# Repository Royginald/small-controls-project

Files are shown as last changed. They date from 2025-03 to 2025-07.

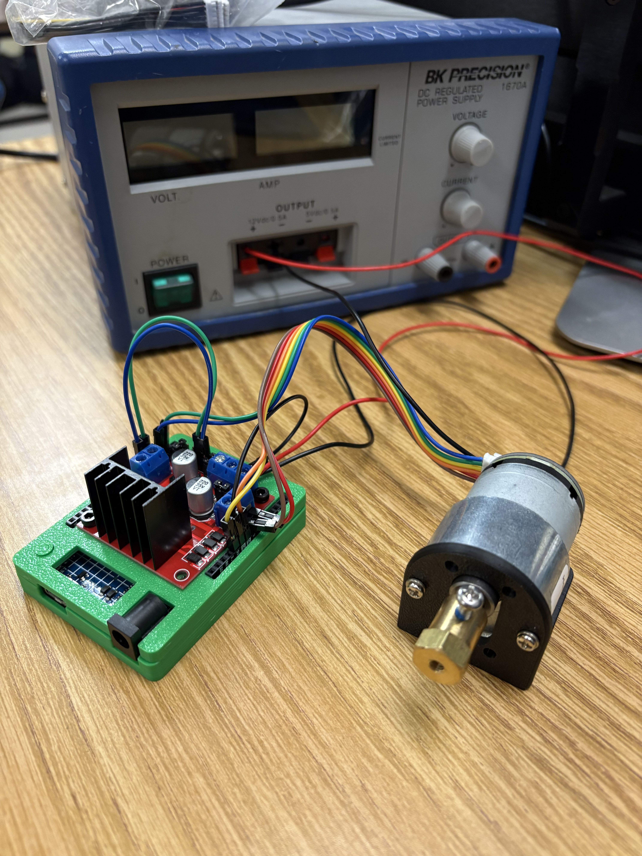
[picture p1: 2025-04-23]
wiring_setup/ArduinoPlant2.jpeg

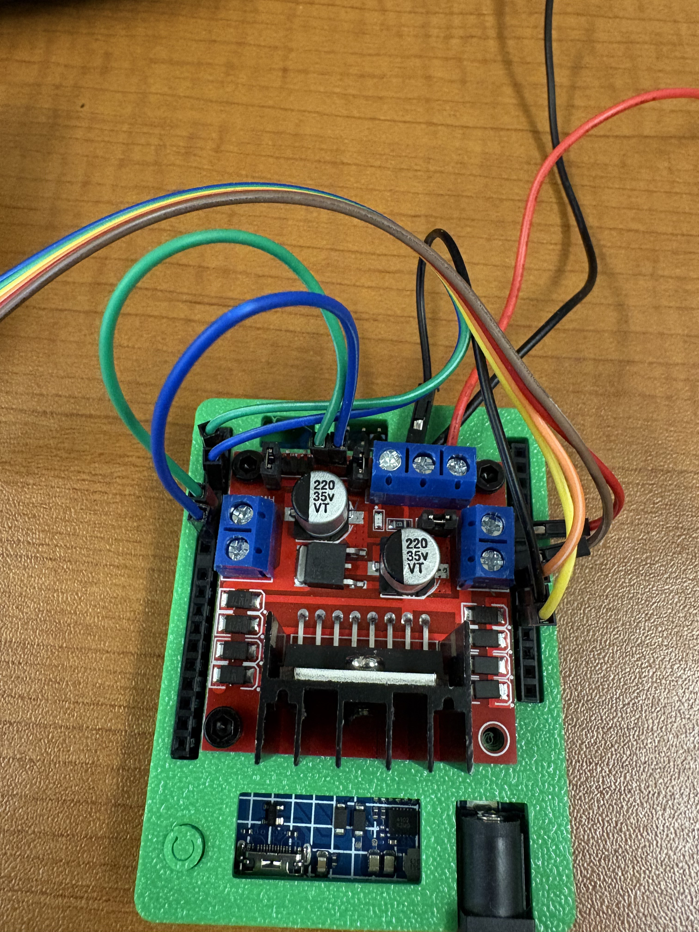
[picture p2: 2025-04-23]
wiring_setup/ArduinoPlant1.jpeg

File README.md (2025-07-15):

This repository documents the motor plants that were made for the use of the Inteligent Controls and Injetion moldling lab an UNB.

This repository conains:
 - The CAD files needed to 3D print the brackets for the motor (cad)
 - The wiring digram used to wire the Arduino R4 to the motor and motor driver (wiring_setup)
 - An Arduino program to control the motor from an Ardino R4 (Motor_Control)
 - Some sample responses (in steps/s) of the motor at various voltages (Motor Responses)
 - A system identification program that can be run from the Ardunio R4 (Sys_ID)
 - A response visualizer that can dispaly the motors response on a PC (serial.comm.py)

For all control algorithums used, the motor is treated as a first order system with the following parameters:

Plant gain: 501.16 steps/s per volt
Plant time constant: 0.16046 seconds

For speed control (Where speed is measured in steps/s):

$T(s) = \frac{501.16}{0.16046 s + 1}$

For position control (Where position is measured in steps):

$T(s) = \frac{501.16}{s(0.16046 s + 1)}$

The encoder has 1320 steps per revolution.

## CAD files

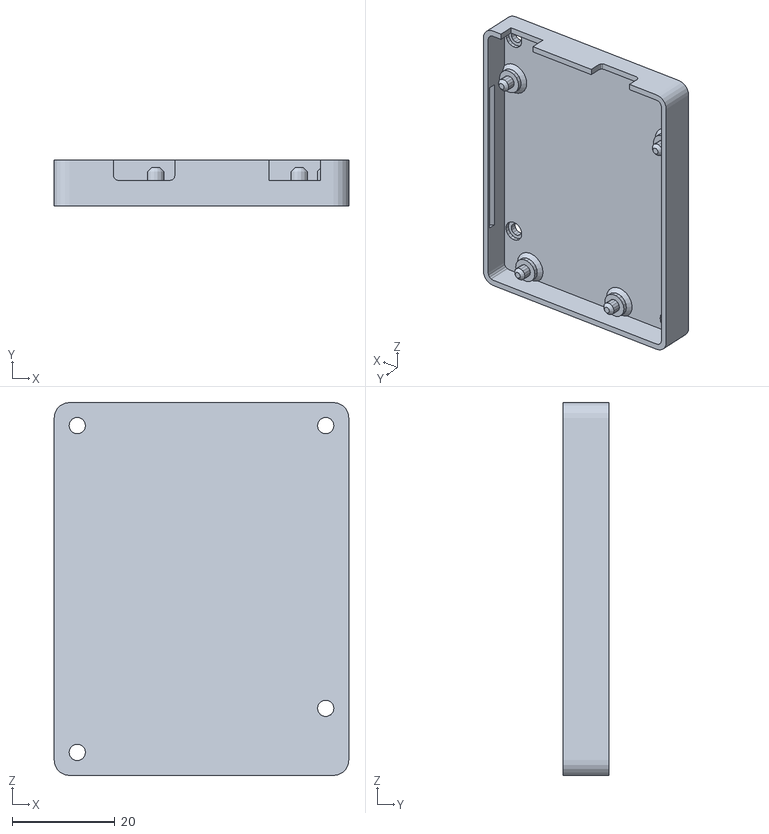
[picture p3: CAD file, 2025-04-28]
cad/!stl/uno_r4_base_3.stl
57.3 x 9.00 x 72.6

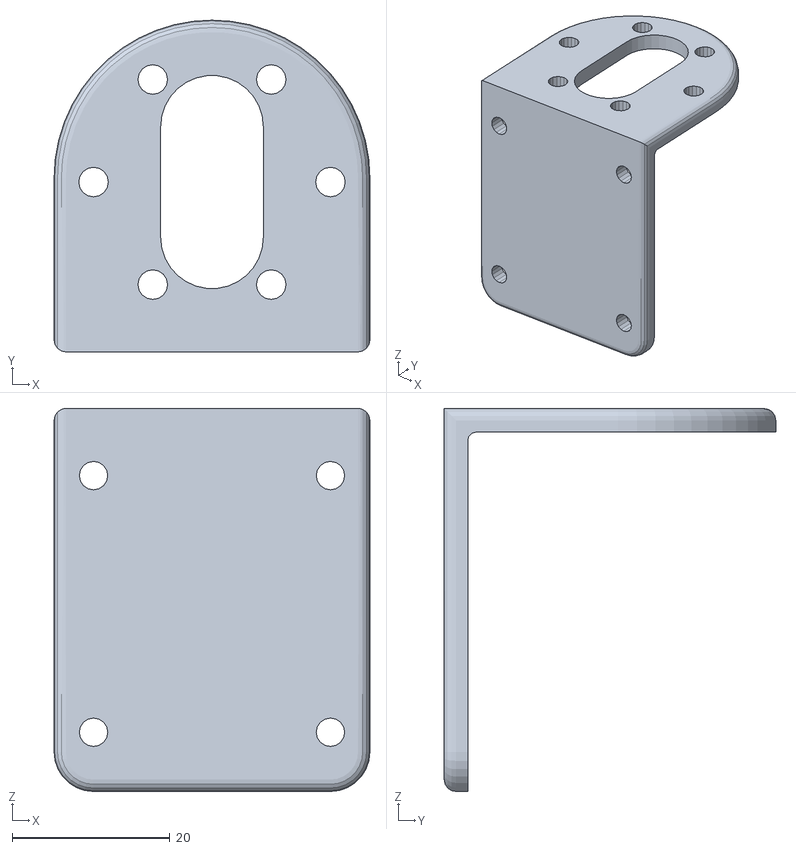
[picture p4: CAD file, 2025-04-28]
cad/!stl/520 DC Gear Motor Bracket.stl
40.0 x 42.0 x 48.5

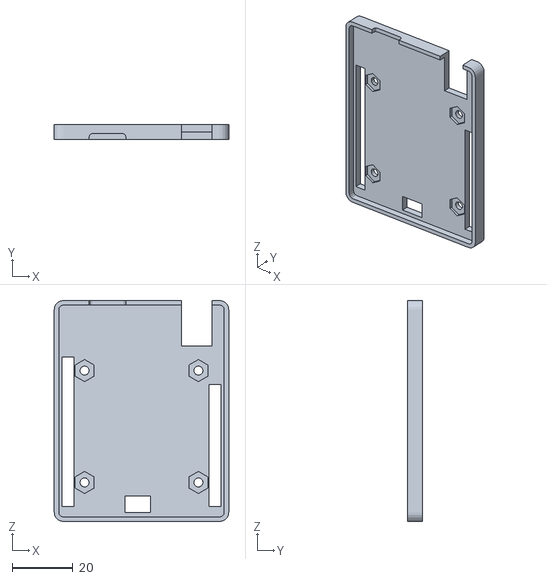
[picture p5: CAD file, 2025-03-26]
cad/!stl/uno_r4_lid.stl
57.3 x 5.00 x 72.6

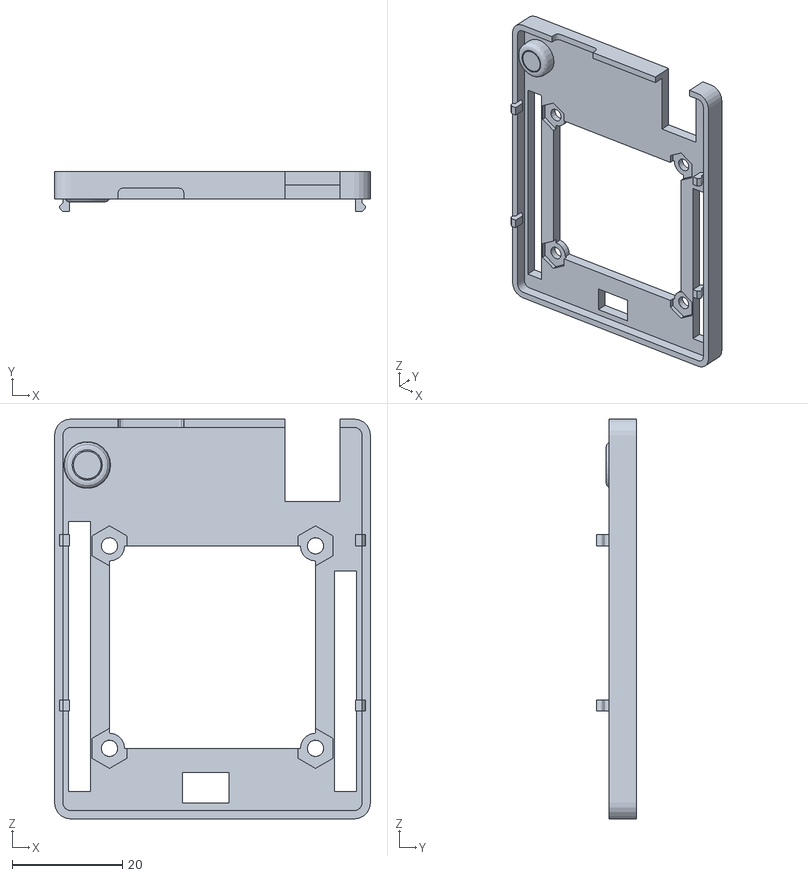
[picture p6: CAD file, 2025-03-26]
cad/!stl/uno_r4_lid_2.stl
57.3 x 7.30 x 72.6

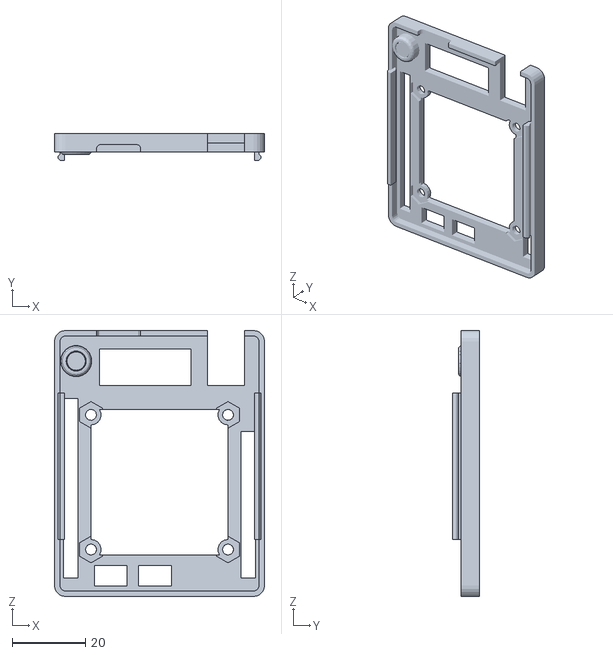
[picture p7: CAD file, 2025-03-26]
cad/!stl/uno_r4_lid_3.stl
57.3 x 7.30 x 72.6

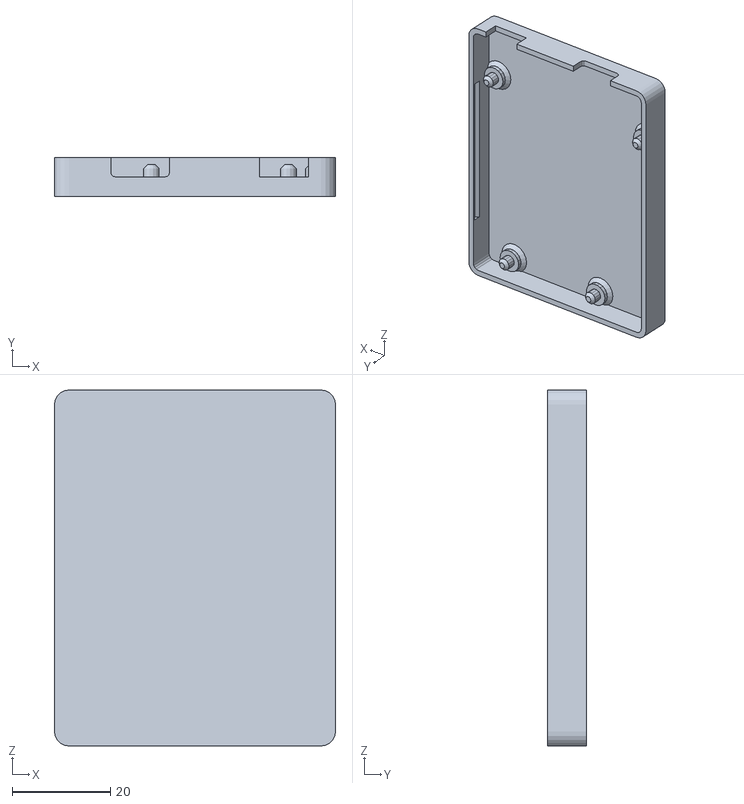
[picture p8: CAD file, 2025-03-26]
cad/!stl/uno_r4_base_2.stl
57.3 x 8.00 x 72.6

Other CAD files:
cad/!stl/uno_r4_base.stl
cad/520 DC Gear Motor Bracket.ipt
cad/L298N Driver DC Motor, Stepper Motor.ipt
cad/OldVersions/motor_plant_assembly.0015.iam
cad/OldVersions/uno_r4_base.0032.ipt
cad/OldVersions/uno_r4_lid.0069.ipt
cad/motor_plant_assembly.iam
cad/uno_r4_base.ipt
cad/uno_r4_lid.ipt

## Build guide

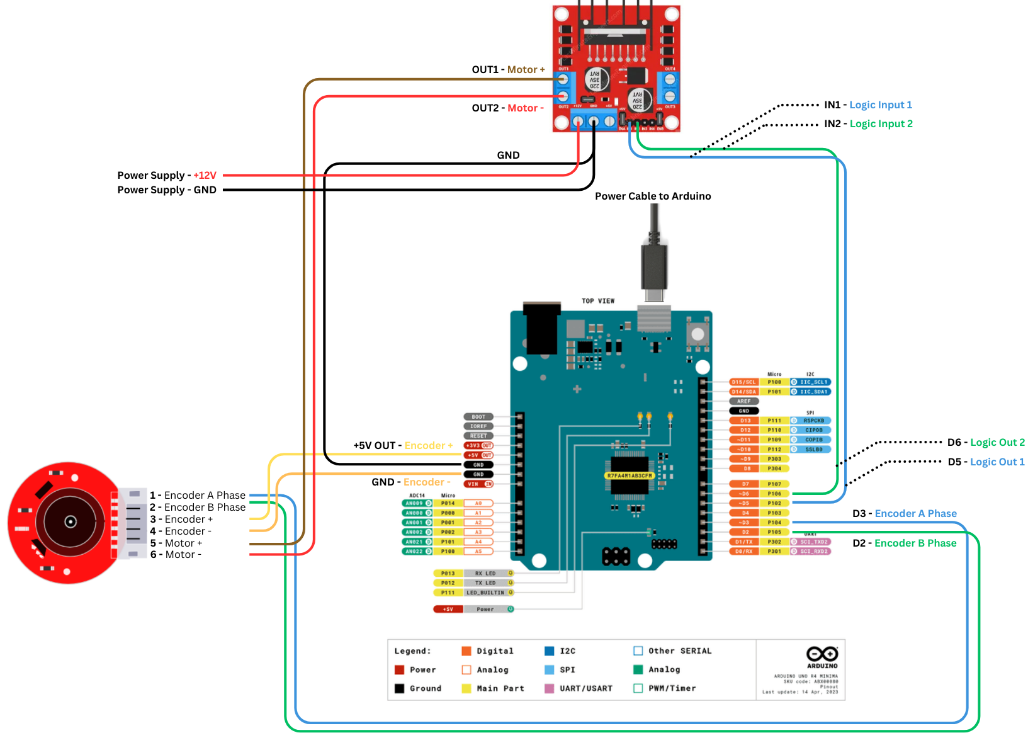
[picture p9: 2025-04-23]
wiring_setup/ArduinoWiring.png

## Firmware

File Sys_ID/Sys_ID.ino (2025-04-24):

// #include "Motor_test.h"
#define TEST_VOLTAGE 6
#define TEST_TIME 5.
#define NUM_DATA_POINTS 1500
#define END_TOL 0.9

#define MOTOR_1_PIN 5
#define MOTOR_2_PIN 6

#define ENCODER_A_PIN 2
#define ENCODER_B_PIN 3

#define MOTOR_MAX_VOLTAGE 12
#define TIME_STEP 0.001

// float setpoint = 0;
// int error, control_action;

volatile long encoderPosition = 0;
// long prev_encoder_pos = 0;
// float speed = 0;

unsigned long loop_start_time, prog_start_time;
double dt = TEST_TIME / NUM_DATA_POINTS;
long data[NUM_DATA_POINTS]; // Steps
float data_diff[NUM_DATA_POINTS - 1]; // Steps per second
float tau;

int i = 0;

void setup() {
    delay(500);

    pinMode(MOTOR_1_PIN, OUTPUT);
    pinMode(MOTOR_2_PIN, OUTPUT);

    attachInterrupt(digitalPinToInterrupt(ENCODER_A_PIN), handleEncoderA, CHANGE);
    attachInterrupt(digitalPinToInterrupt(ENCODER_B_PIN), handleEncoderB, CHANGE);

    Serial.setTimeout(1); //Milliseconds
    Serial.begin(9600);
    
    // prog_start_time = micros();
    loop_start_time = micros();
}

void loop() {
    // if (Serial.available() > 0) {
    //     setpoint = Serial.readString().toFloat();
    // }

    // Collect data
    Serial.println("Starting Test");
    // Serial.println(String(dt));
    analogWrite(MOTOR_1_PIN, TEST_VOLTAGE*255/MOTOR_MAX_VOLTAGE);

    i = 0;

    while(i < NUM_DATA_POINTS) {
        if (dt * 1000000 < (micros() - loop_start_time)) {
            loop_start_time = micros();
            data[i] = getEncoderPosition();
            i++;
        }
    }

    analogWrite(MOTOR_1_PIN, 0);
    Serial.println("Test Finished");
    Serial.println("Starting Processing");

    // Process data
    // Differentate

    for (int j = 0; j < NUM_DATA_POINTS - 1; j++) {
        data_diff[j] = ( data[j+1] - data[j] ) / dt;
    }

    float end_value = float(data_diff[NUM_DATA_POINTS-2]) * END_TOL;

    // Serial.println(data_diff[NUM_DATA_POINTS-2]);
    // Serial.println(END_TOL);
    // Serial.println(end_value);
    // Serial.println(" ------------------ ");

    i = NUM_DATA_POINTS-3;
    while(data_diff[i] > end_value && i >= 0){
        // Serial.println(data_diff[i]);
        i--;
    }

    // Serial.println(i);

    float end_time = i * dt / END_TOL;
    int end_index = i / END_TOL;

    float average = 0;

    for (int j = end_index; j < NUM_DATA_POINTS-2; j++) {
        average += data_diff[j];
    }

    average /= NUM_DATA_POINTS - 1;

    float K_p = average / TEST_VOLTAGE;

    float rise_value = average * 0.63;

    i = end_index;
    while(data_diff[i] > rise_value && i >= 0) {
        i--;
    }

    // float tau = (dt) / (data_diff[i+1] - data_diff[i]) * (rise_value - data_diff[i]) + i * dt;
    tau = i * dt;

    Serial.println("Plant gain: " + String(K_p) + " steps/s / V");
    Serial.print("Plant rise time: ");
    Serial.print(tau, 6);
    Serial.println(" seconds");
    // Serial.println(end_index);
    // Serial.println(i);

    // for (int j = 0; j < NUM_DATA_POINTS-1; j++) {
    //     Serial.print(j * dt);
    //     Serial.print(" ");
    //     Serial.println(data_diff[j]);
    // }

    delay(TEST_TIME * 1000.);

}

long getEncoderPosition() {
    noInterrupts();
    long pos = encoderPosition;
    interrupts();
    return pos;
}

void handleEncoderA() {
    if (digitalRead(ENCODER_A_PIN) == digitalRead(ENCODER_B_PIN)) {
        encoderPosition++;
    } else {
        encoderPosition--;
    }
}

void handleEncoderB() {
    if (digitalRead(ENCODER_A_PIN) != digitalRead(ENCODER_B_PIN)) {
        encoderPosition++;
    } else {
        encoderPosition--;
    }
}

template <typename T> int sgn(T val) {
    return (T(0) < val) - (val < T(0));
}

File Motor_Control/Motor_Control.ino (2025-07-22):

// --------------------------< Main File >--------------------------
// 
// This is the main file of this program which contains the setup() and loop() fucntions
// Each other file is for a specific type of control algorithum
// The control algorithum used and the setpoint are set in this file

#include "Motor_Control.h"
using namespace MPC_Control;

float setpoint = 0;
float control_action;

volatile long encoderPosition = 0;
long prev_encoder_pos = 0;
float speed = 0;

unsigned long loop_start_time, prog_start_time;
long dt = 0;

void setup() {
    delay(500);

    // Set motor PWM pins as output pins
    pinMode(MOTOR_1_PIN, OUTPUT);
    pinMode(MOTOR_2_PIN, OUTPUT);

    // Set up the encoder pins to handel interupts
    attachInterrupt(digitalPinToInterrupt(ENCODER_A_PIN), handleEncoderA, CHANGE);
    attachInterrupt(digitalPinToInterrupt(ENCODER_B_PIN), handleEncoderB, CHANGE);

    // Start a serial connection over USB and set the timeout to 1 ms for fast data transfer
    Serial.setTimeout(1); //Milliseconds
    Serial.begin(9600);
    
    // Track the start of the program and the start of the latest loop
    prog_start_time = micros();
    loop_start_time = micros();
}

void loop() {
    // if (Serial.available() > 0) {
    //     setpoint = Serial.readString().toFloat();
    // }  

    // Find the time since the loop
    dt = float((micros() - loop_start_time)); // Time since last loop in microseconds

    // If the time since the last loop is greater then the time step, calculate a new cotnrol action
    if (dt > TIME_STEP * 1000000) {
        // Reset the loop timer
        loop_start_time = micros();

        // Calculate the current motor speed
        speed = (getEncoderPosition() - prev_encoder_pos)*1000000.0/dt; // Speed of motor, in steps per second
        prev_encoder_pos = getEncoderPosition(); // Position of the motor, in steps

        // Find the angle of the motor shaft in degrees
        long send_pos = getEncoderPosition() % STEPS_PER_REVOLUTION; 
        if (send_pos < 0)
            send_pos += STEPS_PER_REVOLUTION;
        float motor_angle = float(send_pos) * 360. / STEPS_PER_REVOLUTION;

        // Find the feedback based on the feedback type selected
        #ifdef speed_feedback
        float feedback = speed;
        Serial.println(speed);
        #endif

        #ifdef position_feedback
        float feedback = getEncoderPosition();
        Serial.println(getEncoderPosition());
        #endif

        // Calcualte the value of the setpoint based on the time since the program started
        float program_time = float((micros() - prog_start_time)/1000000.); // Runtime in seconds

        #ifdef step_setpoint
        setpoint = step(program_time, 2500.0);
        #endif

        #ifdef ramp_setpoint
        setpoint = ramp(program_time, 80.0);
        #endif

        #ifdef sine_setpoint
        setpoint = sine(program_time, 0.01, 500.0) + 2000;
        #endif  

        // Based on the user selected control algorithum, the control action will be calculated
        // The units of the control action are volts
        #ifdef deadbeat_control
        #endif

        #ifdef MPC_control
        control_action = control_MPC(setpoint, feedback);
        #endif
        
        #ifdef PID_control
        control_action = control_PID(setpoint, feedback);
        #endif

        #ifdef PI_control
        control_action = control_PI(setpoint, feedback);
        #endif

        #ifdef P_control
        control_action = control_P(setpoint, feedback);
        #endif

        #ifdef Fixed_voltage
        control_action = 3;
        #endif   

        // The process variable is printed out via the serial connection
        // Serial.println(control_action);
        // Serial.println(program_time);
        // Serial.println(getEncoderPosition());
        // Serial.print("Meas: "); Serial.print(speed);
        // Serial.print(",Setpoint: "); Serial.println(setpoint);
        // Serial.println(speed);

        // Serial.println(int(float(send_pos) * 360. / STEPS_PER_REVOLUTION));
        // Serial.println(getEncoderPosition());
        // Serial.println(speed);

        // Limit the control action if it is above the maximum voltage of the motor driver
        if (abs(control_action) > MOTOR_MAX_VOLTAGE) {
            control_action = MOTOR_MAX_VOLTAGE * sgn(control_action);
        }

        // Send the control action to the motor driver while accounting for its sign
        if (control_action > 0) {
            analogWrite(MOTOR_1_PIN, control_action*255/MOTOR_MAX_VOLTAGE);
            analogWrite(MOTOR_2_PIN, 0);
        } else {
            analogWrite(MOTOR_1_PIN, 0);
            analogWrite(MOTOR_2_PIN, -control_action*255/MOTOR_MAX_VOLTAGE);
        }
    }
}

// Function to get the position of the encoder
long getEncoderPosition() {
    noInterrupts();
    long pos = encoderPosition;
    interrupts();
    return pos;
}

// Function to add or subtract some nubmer of steps from the encoder position
void addEncoderPosition(long add) {
    noInterrupts();
    encoderPosition += add;
    interrupts();
    // return pos;
}

// Interupt service routine for the first pin of the encoder
void handleEncoderA() {
    if (digitalRead(ENCODER_A_PIN) == digitalRead(ENCODER_B_PIN)) {
        encoderPosition++;
    } else {
        encoderPosition--;
    }
}

// Interupt service routine for the second pin of the encoder
void handleEncoderB() {
    if (digitalRead(ENCODER_A_PIN) != digitalRead(ENCODER_B_PIN)) {
        encoderPosition++;
    } else {
        encoderPosition--;
    }
}

// Template for an absolute value fucntion
template <typename T> int sgn(T val) {
    return (T(0) < val) - (val < T(0));
}

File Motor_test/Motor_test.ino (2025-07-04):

#include "Motor_test.h"
using namespace MPC_Control;

float setpoint = 0;
float control_action;

volatile long encoderPosition = 0;
long prev_encoder_pos = 0;
float speed = 0;

unsigned long loop_start_time, prog_start_time;
long dt = 0;

void setup() {
    delay(500);

    pinMode(MOTOR_1_PIN, OUTPUT);
    pinMode(MOTOR_2_PIN, OUTPUT);

    attachInterrupt(digitalPinToInterrupt(ENCODER_A_PIN), handleEncoderA, CHANGE);
    attachInterrupt(digitalPinToInterrupt(ENCODER_B_PIN), handleEncoderB, CHANGE);

    Serial.setTimeout(1); //Milliseconds
    Serial.begin(9600);
    
    prog_start_time = micros();
    loop_start_time = micros();
}

void loop() {
    // if (Serial.available() > 0) {
    //     setpoint = Serial.readString().toFloat();
    // }

    setpoint = step(float((micros() - prog_start_time)/1000), 1500.0);
    // setpoint = sine(float((micros() - prog_start_time)/1000), 0.01, 500.0) + 2000;
    // setpoint = ramp(float((micros() - prog_start_time)/1000000), 50.0);

    dt = (micros() - loop_start_time);

    if (dt > (TIME_STEP * 1000000)) {
        loop_start_time = micros();
        speed = (getEncoderPosition() - prev_encoder_pos)*1000000.0/dt;
        prev_encoder_pos = getEncoderPosition();

        long send_pos = getEncoderPosition() % STEPS_PER_REVOLUTION; 
        if (send_pos < 0)
            send_pos += STEPS_PER_REVOLUTION;

        // Serial.println(int(float(send_pos) * 360. / STEPS_PER_REVOLUTION));
        // Serial.println(getEncoderPosition());
        // Serial.println(speed);

        // control_action = control_P(setpoint, getEncoderPosition());
        // control_action = control_PI(setpoint, getEncoderPosition());
        control_action = control_PID(setpoint, getEncoderPosition());
        // control_action = control_MPC(setpoint, getEncoderPosition());
        // control_action = setpoint;
        // control_action = MOTOR_MAX_VOLTAGE;

        // Serial.println(control_action);
        // Serial.println(setpoint);
        Serial.println(getEncoderPosition());
        // Serial.print("Meas: "); Serial.print(speed);
        // Serial.print(",Setpoint: "); Serial.println(setpoint);
        // Serial.println(speed);

        if (abs(control_action) > MOTOR_MAX_VOLTAGE) {
            control_action = MOTOR_MAX_VOLTAGE * sgn(control_action);
        }

        if (control_action > 0) {
            analogWrite(MOTOR_1_PIN, control_action*255/MOTOR_MAX_VOLTAGE);
            analogWrite(MOTOR_2_PIN, 0);
        } else {
            analogWrite(MOTOR_1_PIN, 0);
            analogWrite(MOTOR_2_PIN, -control_action*255/MOTOR_MAX_VOLTAGE);
        }
    }
}

long getEncoderPosition() {
    noInterrupts();
    long pos = encoderPosition;
    interrupts();
    return pos;
}

void addEncoderPosition(long add) {
    noInterrupts();
    encoderPosition += add;
    interrupts();
    // return pos;
}

void handleEncoderA() {
    if (digitalRead(ENCODER_A_PIN) == digitalRead(ENCODER_B_PIN)) {
        encoderPosition++;
    } else {
        encoderPosition--;
    }
}

void handleEncoderB() {
    if (digitalRead(ENCODER_A_PIN) != digitalRead(ENCODER_B_PIN)) {
        encoderPosition++;
    } else {
        encoderPosition--;
    }
}

template <typename T> int sgn(T val) {
    return (T(0) < val) - (val < T(0));
}

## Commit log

2025-03-25 made case for arduino
    [L298N Driver DC Motor, Stepper Motor.ipt, motor_plant_assembly.0008.iam, motor_plant_assembly.iam, uno_r4_base.0025.ipt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]
2025-03-25 updated lid and base design for 3D print
    [motor_plant_assembly.0008.iam, motor_plant_assembly.0010.iam, motor_plant_assembly.iam, uno_r4_base.stl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]
2025-03-25 remove surface below motor driver, added reset button
    [motor_plant_assembly.0010.iam, motor_plant_assembly.0013.iam, motor_plant_assembly.iam, uno_r4_base.0025.ipt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]
2025-03-25 added cut outs to see LEDs
    [uno_r4_lid.0066.ipt, uno_r4_lid.0069.ipt, uno_r4_lid.ipt, uno_r4_lid_3.stl]
2025-03-26 Added Data logging python file
    [motor_data.csv]
2025-03-26 Enabled sending setpoint to the UNO
    [motor_data.csv]
2025-03-27 Added a file and some changes to do system identification on the motor
    [motor_data.csv, motor_data_10_volts.csv, motor_data_11_volts.csv, motor_data_12_volts.csv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]
2025-04-14 Finished Sys ID script and added wiring info
2025-04-23 modified base with mounting holes (M3 bolts)
    [motor_plant_assembly.0013.iam, motor_plant_assembly.0015.iam, motor_plant_assembly.iam, uno_r4_base.0027.ipt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]
2025-04-28 added bracket stl
    [520 DC Gear Motor Bracket.stl]
2025-04-28 hid a sketch on this .ipt
    [uno_r4_base.ipt]
2025-04-28 stl with M3 holes
    [uno_r4_base_3.stl]
2025-04-28 .ipt for bracket
    [520 DC Gear Motor Bracket.ipt]
2025-04-28 hid a sketch
    [uno_r4_base.0031.ipt, uno_r4_base.0032.ipt]
2025-06-16 Added continuous plotting to the python script
    [motor_data.csv]
2025-06-27 changed variables to be user-defined outside of header. added a print array function that hopefully works
2025-06-27 changed max voltage to float, included MPC
2025-06-27 various debug print statements. issue with the time value being used in the setpoint functions, corrected it
2025-07-04 fixed 'loop_start_time' on step setpoint, added max voltage control action
2025-07-05 Comments and Name change
    Added comments and changed the main file name from Motor_test to Motor_Control
2025-07-06 Added a settings.h file to easily change global control settings
    Also moved sys_id python script to where the motor response are stored. Added some basic information to the README.
2025-07-22 Found all gains for P, PI, and PID control
    Added a python script to calculate the gains for speed and position feedback with P, PI, and PID control. Also made a python script to simulate a systems response and put the calculated gains in the 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
